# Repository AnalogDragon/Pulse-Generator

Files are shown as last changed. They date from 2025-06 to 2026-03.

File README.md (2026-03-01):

**Pulse Generator**  
  
[中文](./README-zh.md)  

Used for testing and calibrating dose rate instruments such as survey meters or calibrators. STM32G0, KiCad.  
  
This device was built because I purchased a LUDLUM Model 3 and a Model 2360, both of which require calibration of multiple threshold levels, so I made this small tool for that purpose.  
  
Functions:  
- 1. Generates adjustable pulses with amplitude 2 mV–1000 mV, pulse width 50 nS–500 µS, adjustable frequency, and selectable positive/negative polarity, for calibration or performance verification;  
- 2. Multiple operating modes;  
- 3. Output interface changed to MHV connector (previous low-quality BNC connectors could suffer dielectric breakdown);  
- 4. Supports USB power supply and battery power; when USB is connected, the battery is automatically disconnected;  

## Buttons  

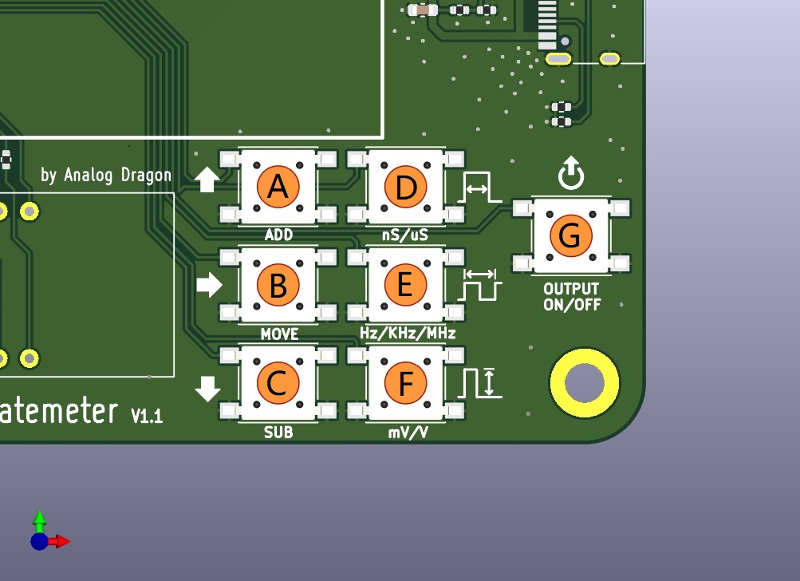
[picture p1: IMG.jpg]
keys
  

**Button function description**  

- A: **Increment** button. When a digit is selected, pressing it increases the value by +1;  
- B: **Select / Mode** button. **Short press** switches the selected digit position; **long press** switches the **mode** (see [Modes](#modes));  
- C: **Decrement** button. When a digit is selected, pressing it decreases the value by −1;  
- D: **Pulse Width** button. Short press to set, long press to change the multiplier. Range: 500 µS–50 nS, minimum step 50 nS, 4 significant digits;  
- E: **Frequency** button. Short press to set, long press to change the multiplier. Range: 5 MHz–0.1 Hz, 3 or 4 significant digits;  
- F: **Voltage** button. Short press to set, long press to switch between **output pulse voltage** and **input high-voltage value**;  
- G: **Output** button. Press to start outputting the configured pulses;  

***Other operations***  
- A + B: Switch output pulse polarity to **positive polarity** pulses (display shows `POS_┌┐_`)  
- C + B: Switch output pulse polarity to **negative polarity** pulses (display shows `NEG‾└┘‾`)  

***High-voltage calibration***  
How to enter: during power-on, hold F + B to enter calibration mode.  

Single-point calibration by default. You can press D / E / F to switch the number of calibration points to 1 / 3 / 5 (updated in V1.2).  
During calibration, adjust the displayed voltage to match the input voltage. Keep the voltage unchanged, then long-press the **Output** button (G) to save the calibration point.  
After the required number of calibration points is saved, calibration ends automatically. If the result displays `DONE`, calibration is successful. If `FAILED RETRY` is displayed, calibration has failed.  

Possible reasons for calibration failure:  
- The voltage difference between calibration points is less than 100 V (for example, point 1 is 100 V and point 2 is 150 V);  
- No input voltage during calibration;  
- The input voltage is not correlated with the displayed voltage;  

## Modes  

Three modes are supported:  

- Normal mode (`NORMAL MODE`): the configured parameters output **continuous** pulses. During output, a rapidly blinking indicator appears at the lower-right corner of the display to show status;  
- Repeat burst mode (`REPEAT BURST`): the configured parameters are output at **100 CPS**;  
- Single burst mode (`SINGEL BURST`): with the configured parameters, each press of the **Output** button generates exactly **100 pulses**;  

## Schematic  

[Schematic](./SCH.pdf)  

## Hardware  

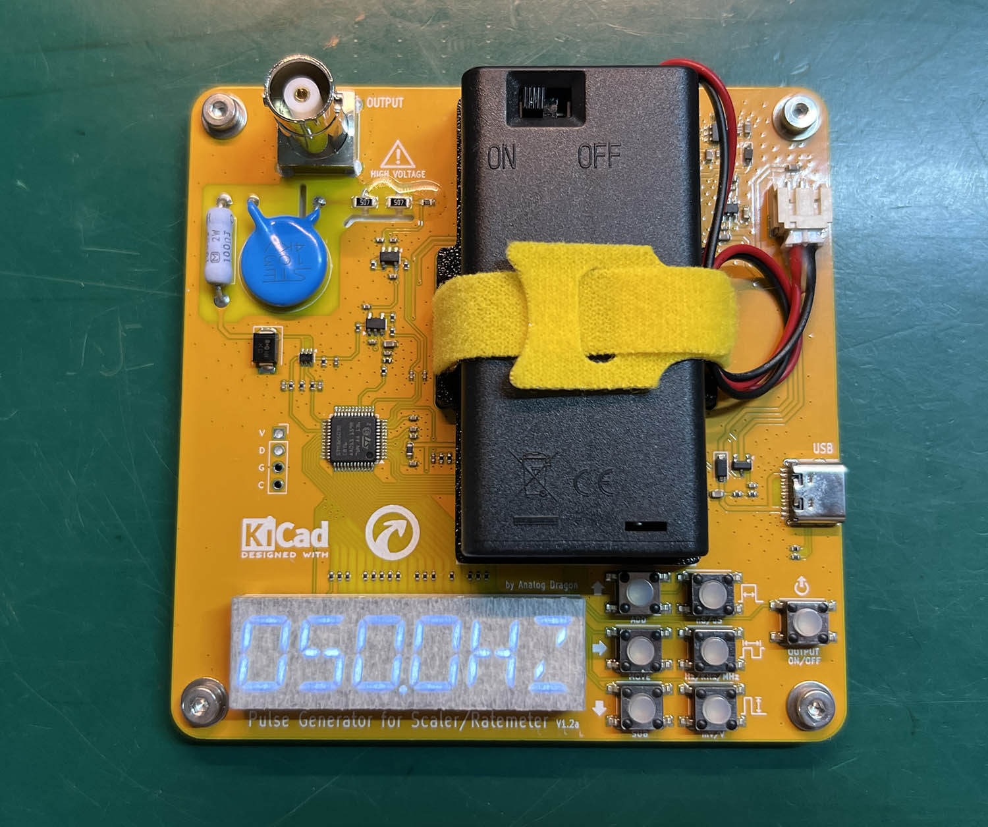
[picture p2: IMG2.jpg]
  

## TEST  
- Normal mode set 1.67CPS(100KCPM)  
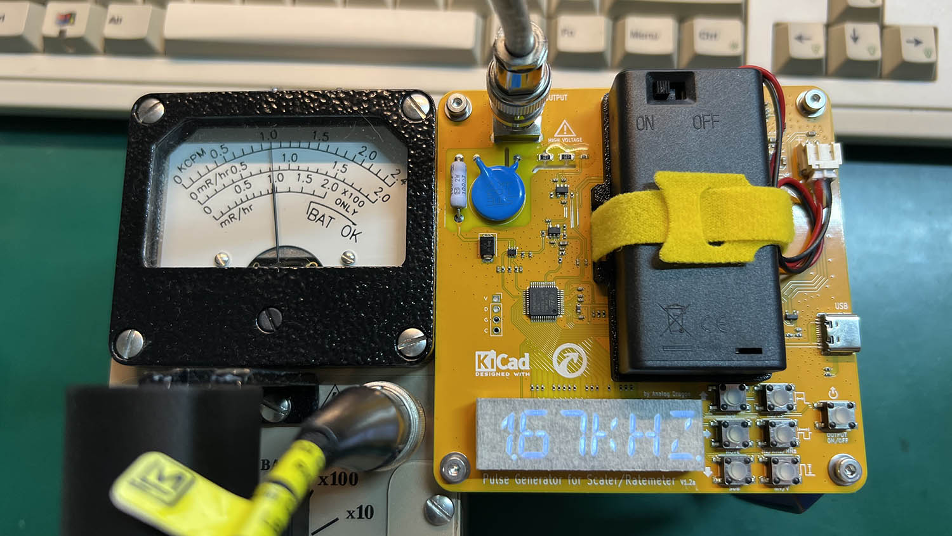
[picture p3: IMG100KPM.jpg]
  
  
- Repeat burst mode (6KCPM)  
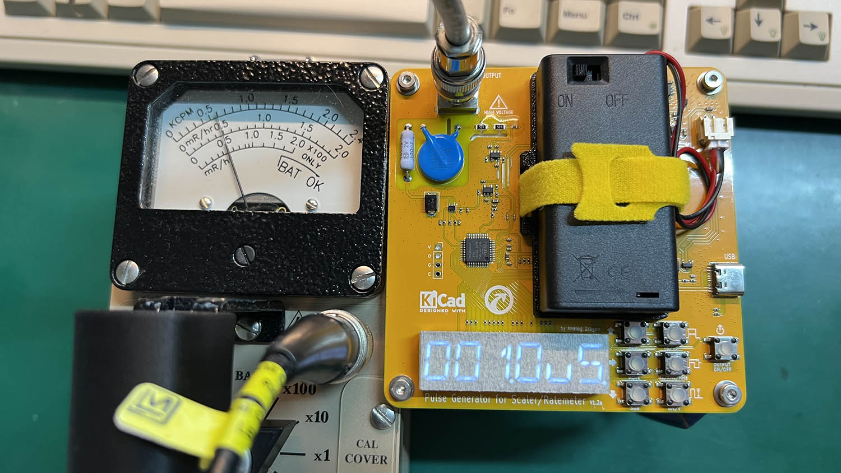
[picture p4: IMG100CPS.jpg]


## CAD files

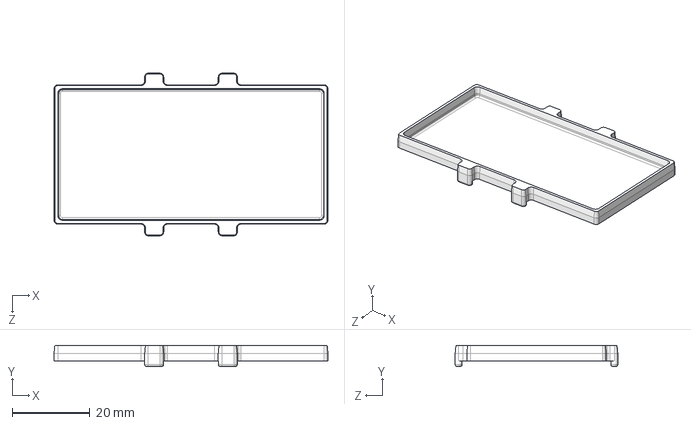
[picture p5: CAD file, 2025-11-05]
3D/电池盒限位small.STEP
70.4 x 5.40 x 41.8 mm

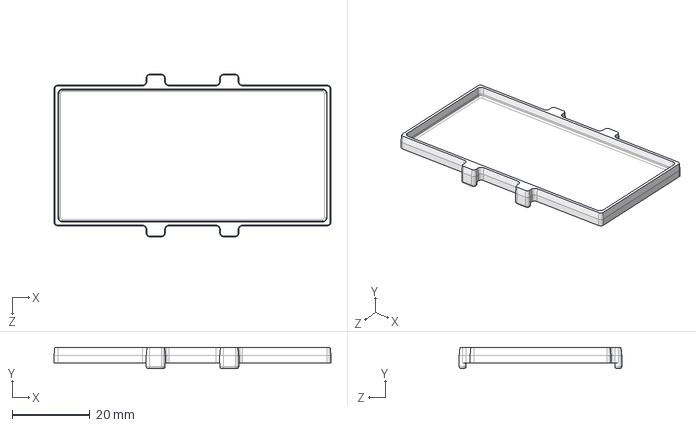
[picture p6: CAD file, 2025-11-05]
3D/电池盒限位.STEP
71.2 x 5.40 x 41.8 mm

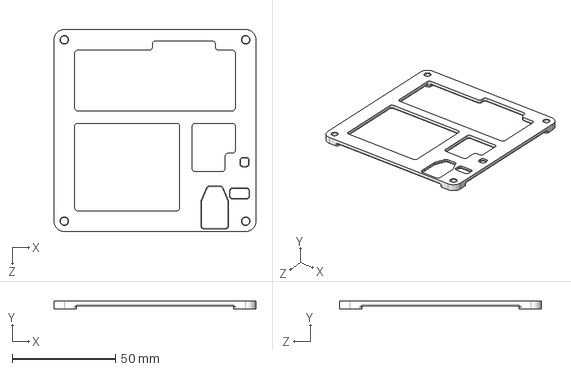
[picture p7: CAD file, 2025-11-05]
3D/底部支架.STEP
98.0 x 4.00 x 98.0 mm

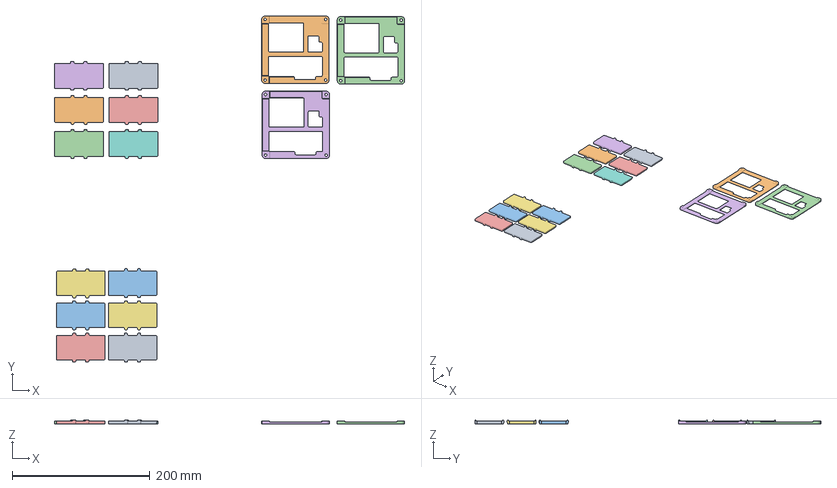
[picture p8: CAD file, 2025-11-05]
3D/print3D.3mf
508.8 x 502.4 x 5.40 mm
零件1.3.STEP x 6
底部支架.STEP x 3
电池盒限位small.STEP x 6

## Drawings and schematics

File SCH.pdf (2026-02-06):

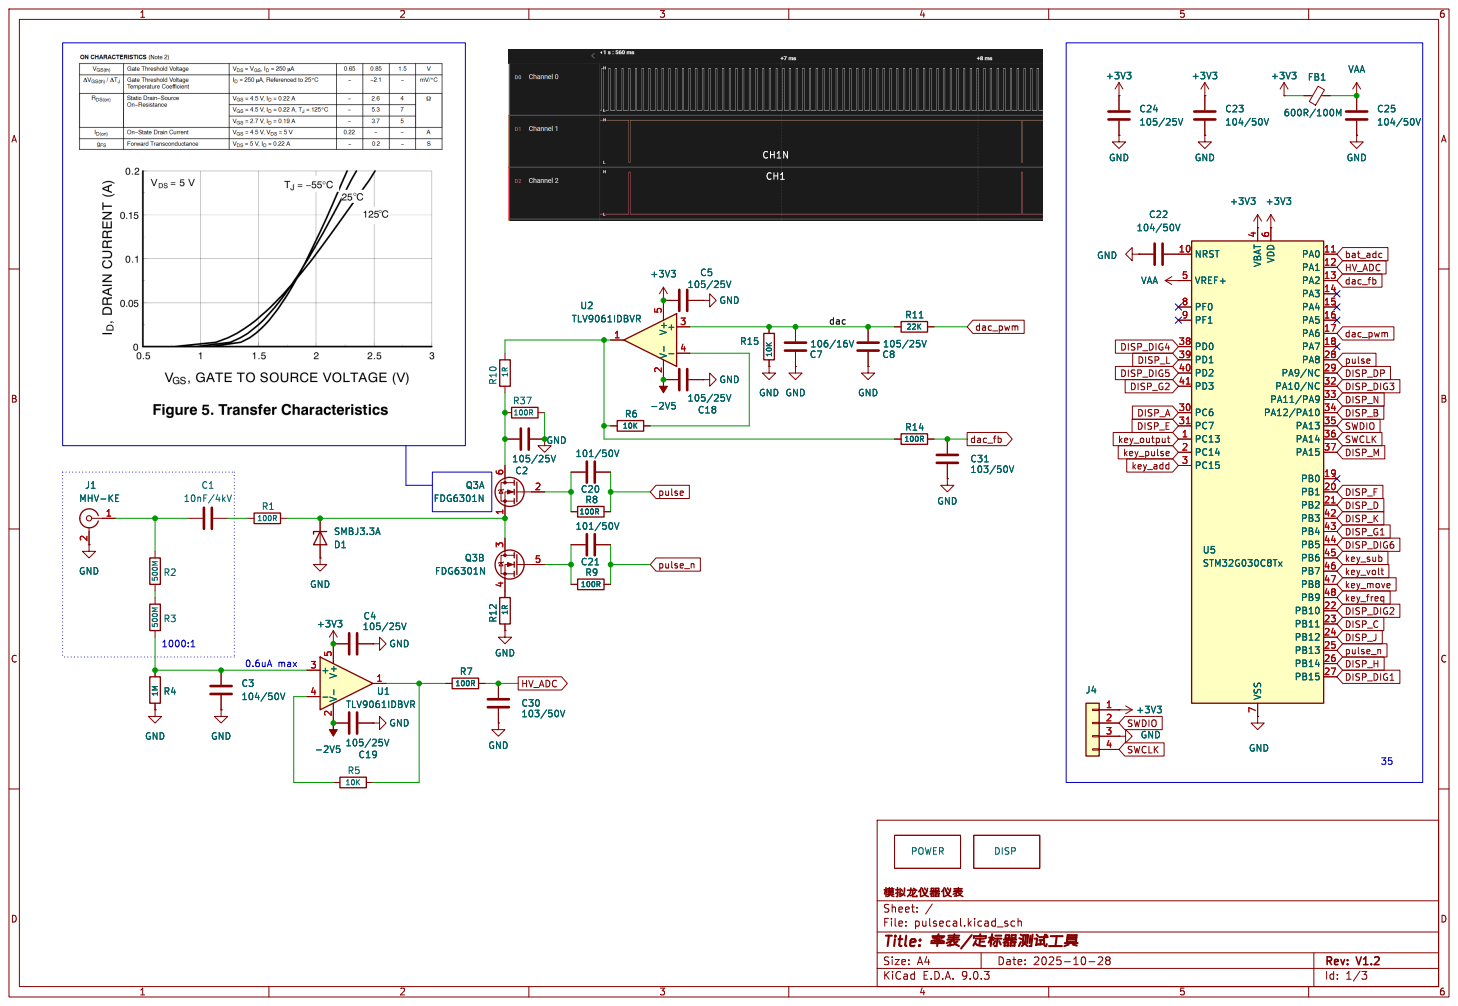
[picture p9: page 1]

File: pulsecal.kicad_sch Sheet: / þÿj!bßŸ™NêVhNêˆh

Id: 1/3 Title: þÿs‡ˆh/[šhVhmK‹Õ]åQw

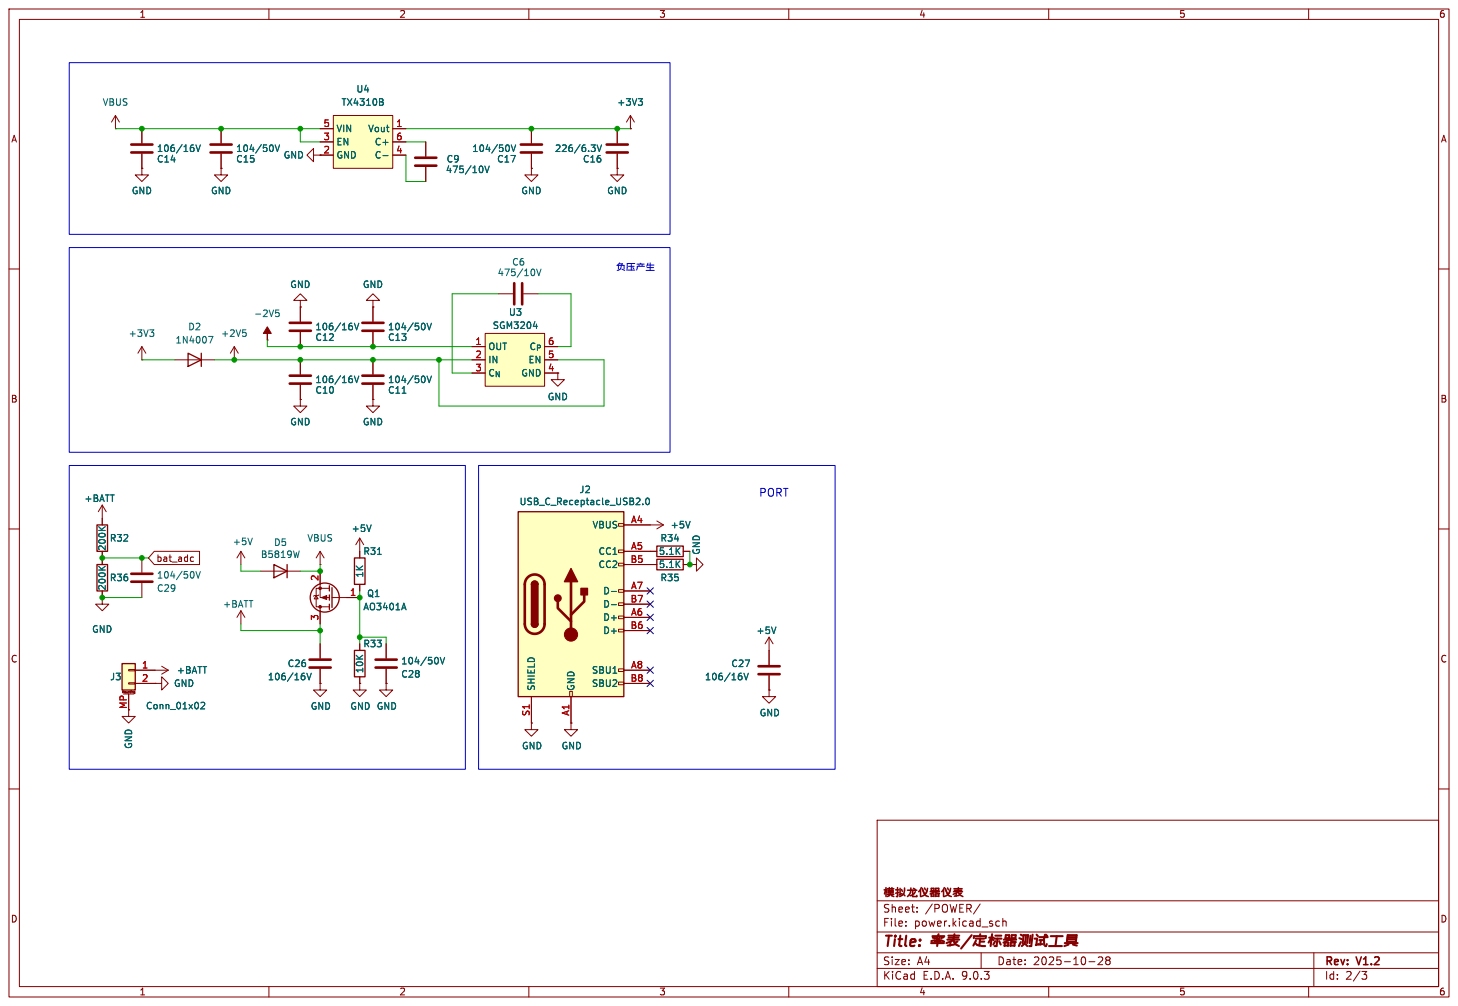
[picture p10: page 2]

File: power.kicad_sch Sheet: /POWER/ þÿj!bßŸ™NêVhNêˆh GND

Id: 2/3 Title: þÿs‡ˆh/[šhVhmK‹Õ]åQw

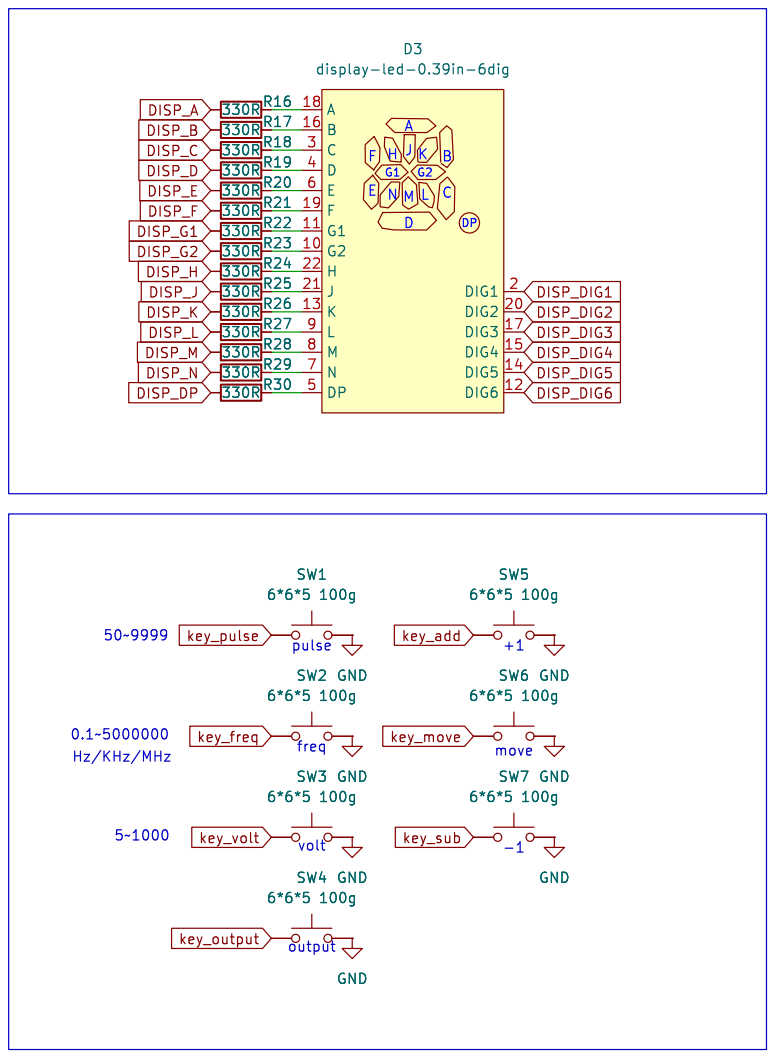
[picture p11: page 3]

6*6*5 100g GND GND GND GND

File: disp.kicad_sch Sheet: /DISP/ þÿj!bßŸ™NêVhNêˆh

Id: 3/3 Title: þÿs‡ˆh/[šhVhmK‹Õ]åQw

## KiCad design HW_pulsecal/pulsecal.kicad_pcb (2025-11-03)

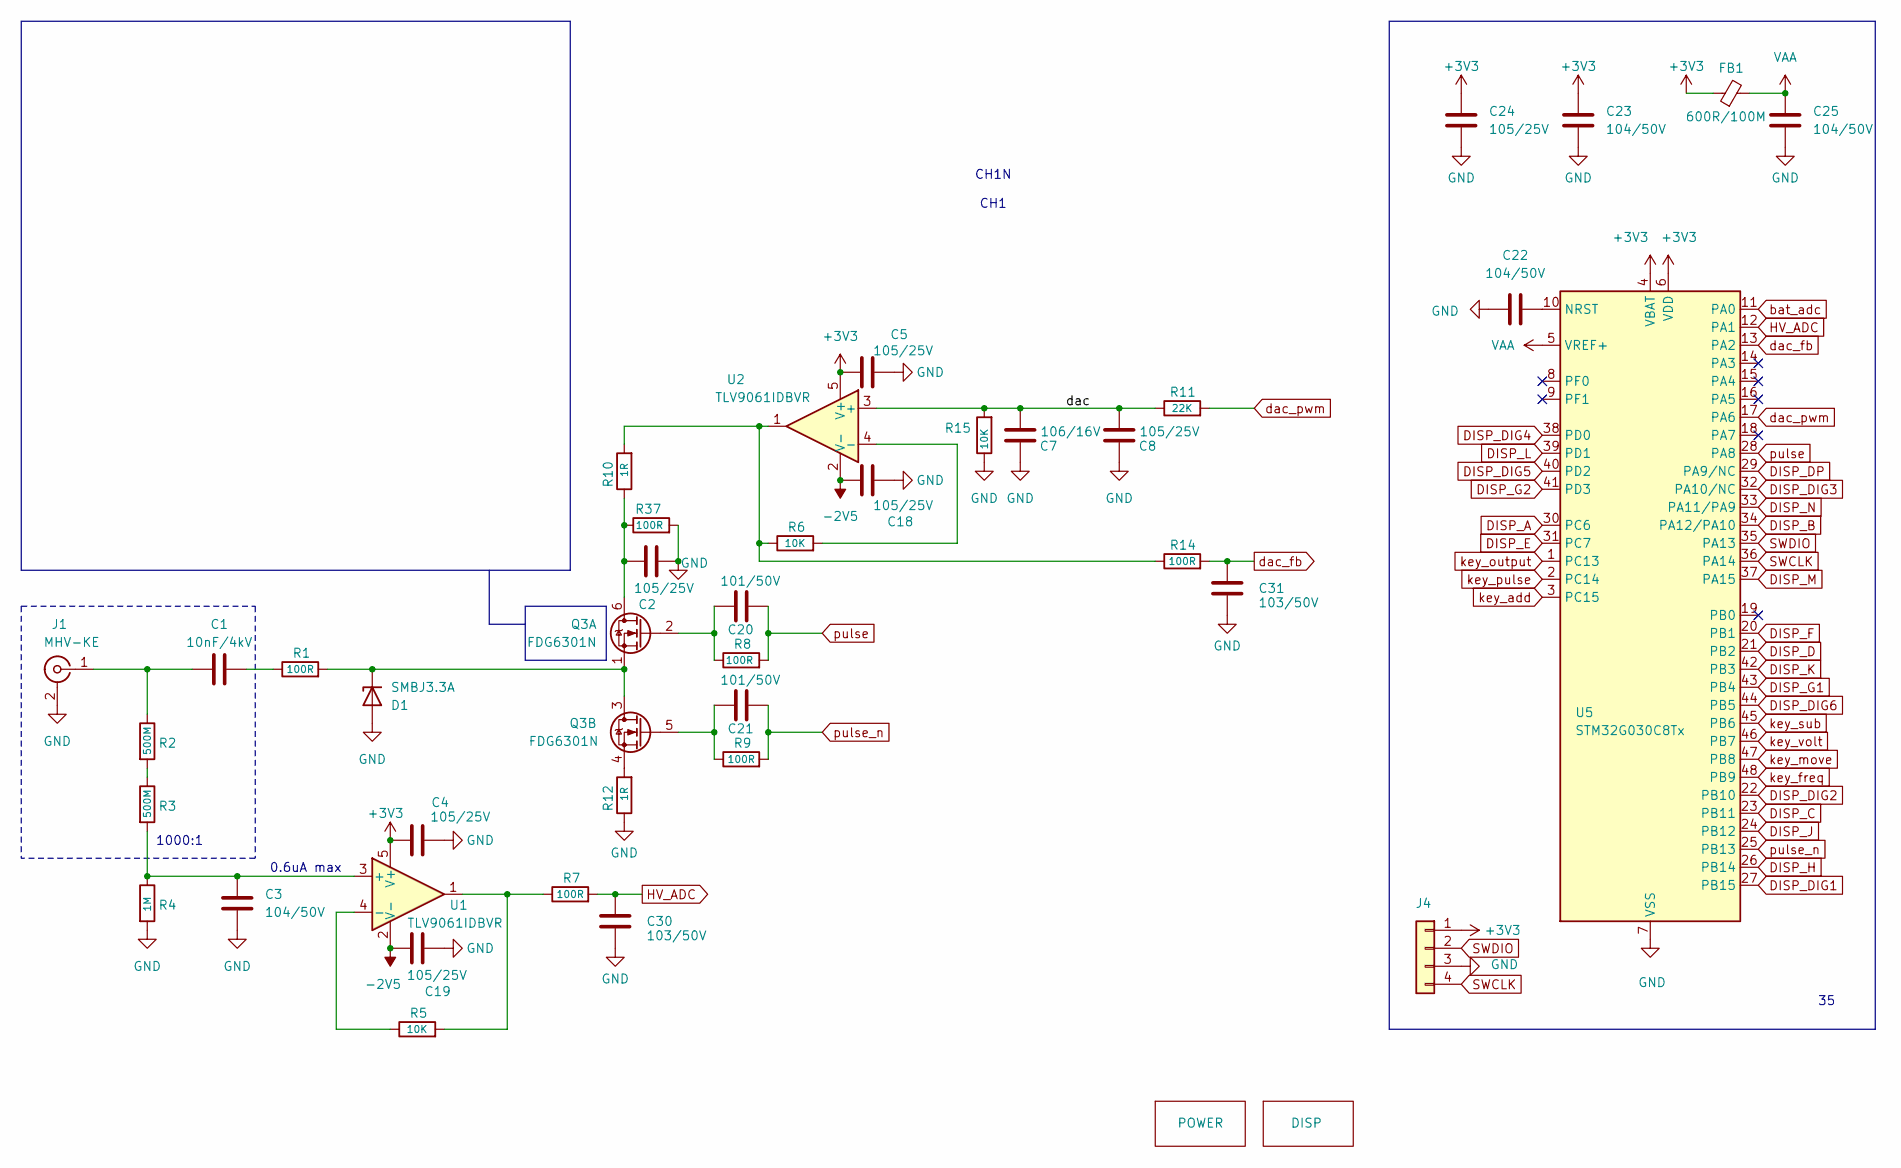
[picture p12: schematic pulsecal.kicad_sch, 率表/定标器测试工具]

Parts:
C1: 10nF/4kV; C_Rect_L13.5mm_W4.0mm_P10.00mm_FKS3_FKP3_MKS4
C2, C4, C5, C8, C18, C19, C24: 105/25V; C_0402_1005Metric
C3, C22, C23, C25: 104/50V; C_0402_1005Metric
C7: 106/16V; C_0603_1608Metric
C20, C21: 101/50V; C_0402_1005Metric
C30, C31: 103/50V; C_0402_1005Metric
D1: SMBJ3.3A; D_SMB
FB1: 600R/100M; L_0603_1608Metric
J1: MHV-KE; BNC_TEConnectivity_1478204_Vertical
J4: Conn_01x04; PinSocket_1x04_P2.54mm_Vertical
Q3: FDG6301N; SOT-363_SC-70-6
R1: 100R; R_Axial_DIN0411_L9.9mm_D3.6mm_P15.24mm_Horizontal
R2, R3: 500M; R_1206_3216Metric
R4: 1M; R_0603_1608Metric
R5, R6, R15: 10K; R_0402_1005Metric
R7, R8, R9, R14, R37: 100R; R_0402_1005Metric
R10, R12: 1R; R_0402_1005Metric
R11: 22K; R_0402_1005Metric
U1, U2: TLV9061IDBVR; SOT-23-5
U5: STM32G030C8Tx; LQFP-48_7x7mm_P0.5mm

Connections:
+3V3: C4.1, C5.1, C23.2, C24.2, FB1.1, J4.1, U1.5 (V+), U2.5 (V+), U5.4 (VBAT), U5.6 (VDD); also elsewhere on the board
-2V5: C18.1, C19.1, U1.2 (V-), U2.2 (V-); also elsewhere on the board
/dac: C7.2, C8.2, R11.1, R15.2, U2.3 (+)
DISP_A: U5.30 (PC6); also elsewhere on the board
DISP_B: U5.34 (PA12/PA10); also elsewhere on the board
DISP_C: U5.23 (PB11); also elsewhere on the board
DISP_D: U5.21 (PB2); also elsewhere on the board
DISP_DIG1: U5.27 (PB15); also elsewhere on the board
DISP_DIG2: U5.22 (PB10); also elsewhere on the board
DISP_DIG3: U5.32 (PA10/NC); also elsewhere on the board
DISP_DIG4: U5.38 (PD0); also elsewhere on the board
DISP_DIG5: U5.40 (PD2); also elsewhere on the board
DISP_DIG6: U5.44 (PB5); also elsewhere on the board
DISP_DP: U5.29 (PA9/NC); also elsewhere on the board
DISP_E: U5.31 (PC7); also elsewhere on the board
DISP_F: U5.20 (PB1); also elsewhere on the board
DISP_G1: U5.43 (PB4); also elsewhere on the board
DISP_G2: U5.41 (PD3); also elsewhere on the board
DISP_H: U5.26 (PB14); also elsewhere on the board
DISP_J: U5.24 (PB12); also elsewhere on the board
DISP_K: U5.42 (PB3); also elsewhere on the board
DISP_L: U5.39 (PD1); also elsewhere on the board
DISP_M: U5.37 (PA15); also elsewhere on the board
DISP_N: U5.33 (PA11/PA9); also elsewhere on the board
GND: C2.2, C3.2, C4.2, C5.2, C7.1, C8.1, C18.2, C19.2, C22.1, C23.1, C24.1, C25.1, C30.1, C31.1, D1.2 (A), J1.2 (Ext), J4.3, R4.2, R12.1, R15.1, R37.2, U5.7 (VSS); also elsewhere on the board
HV_ADC: C30.2, R7.2, U5.12 (PA1)
unnamed: C1.2, R1.1
unnamed: D1.1 (K), Q3.1 (S), Q3.3 (D), R1.2
unnamed: C1.1, J1.1 (In), R2.1
unnamed: C2.1, Q3.6 (D), R10.1, R37.1
unnamed: C20.2, Q3.2 (G), R8.1
unnamed: C21.2, Q3.5 (G), R9.1
unnamed: Q3.4 (S), R12.2
unnamed: R2.2, R3.1
unnamed: R5.2, R7.1, U1.1
unnamed: R6.1, R10.2, R14.1, U2.1
unnamed: C3.1, R3.2, R4.1, U1.3 (+)
unnamed: R5.1, U1.4 (-)
unnamed: R6.2, U2.4 (-)
unnamed: C22.2, U5.10 (NRST)
SWCLK: J4.4, U5.36 (PA14)
SWDIO: J4.2, U5.35 (PA13)
VAA: C25.2, FB1.2, U5.5 (VREF+)
bat_adc: U5.11 (PA0); also elsewhere on the board
dac_fb: C31.2, R14.2, U5.13 (PA2)
dac_pwm: R11.2, U5.17 (PA6)
key_add: U5.3 (PC15); also elsewhere on the board
key_freq: U5.48 (PB9); also elsewhere on the board
key_move: U5.47 (PB8); also elsewhere on the board
key_output: U5.1 (PC13); also elsewhere on the board
key_pulse: U5.2 (PC14); also elsewhere on the board
key_sub: U5.45 (PB6); also elsewhere on the board
key_volt: U5.46 (PB7); also elsewhere on the board
pulse: C20.1, R8.2, U5.28 (PA8)
pulse_n: C21.1, R9.2, U5.25 (PB13)

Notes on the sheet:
0.6uA max
CH1N CH1
1000:1

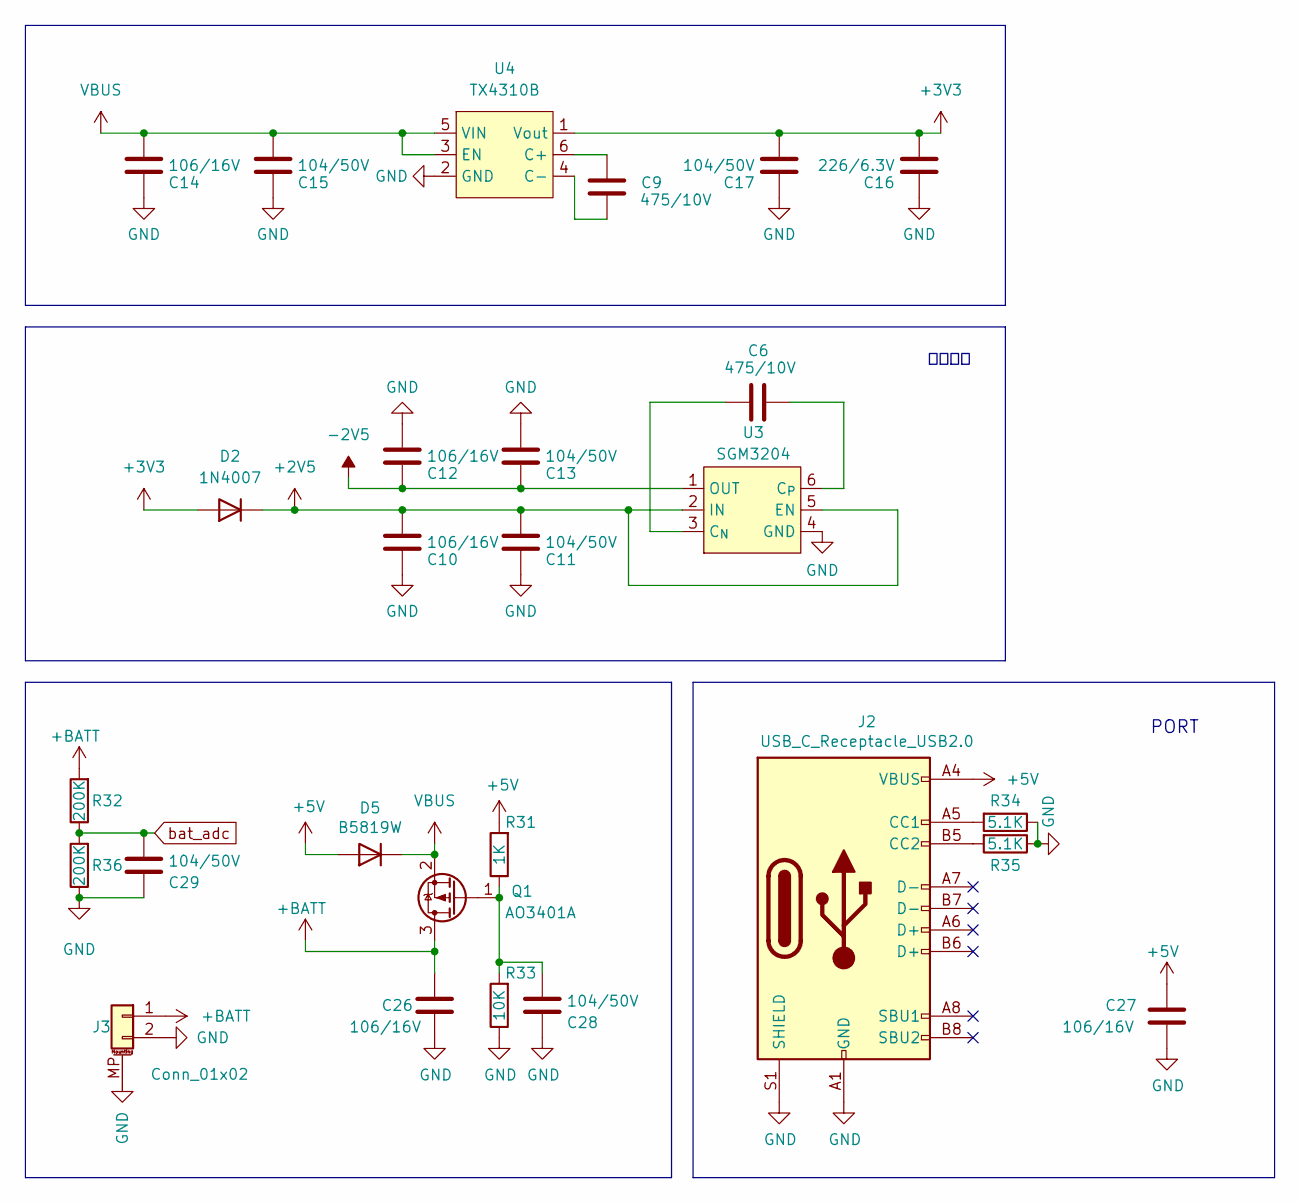
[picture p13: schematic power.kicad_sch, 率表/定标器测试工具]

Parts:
C6, C9: 475/10V; C_0603_1608Metric
C10, C12, C14, C26, C27: 106/16V; C_0603_1608Metric
C11, C13, C15, C17, C28, C29: 104/50V; C_0402_1005Metric
C16: 226/6.3V; C_0603_1608Metric
D2: 1N4007; D_SOD-323_HandSoldering
D5: B5819W; D_SOD-123
J2: USB_C_Receptacle_USB2.0; USB_C_Receptacle_HRO_TYPE-C-31-M-12
J3: Conn_01x02; JST_PH_S2B-PH-SM4-TB_1x02-1MP_P2.00mm_Horizontal
Q1: AO3401A; SOT-23
R31: 1K; R_0402_1005Metric
R32, R36: 200K; R_0402_1005Metric
R33: 10K; R_0402_1005Metric
R34, R35: 5.1K; R_0402_1005Metric
U3: SGM3204; SOT-23-6
U4: TX4310B; SOT-23-6

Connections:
+2V5: C10.1, C11.1, D2.1 (K), U3.2 (IN), U3.5 (EN)
+3V3: C16.1, C17.1, D2.2 (A), U4.1 (Vout); also elsewhere on the board
+5V: C27.1, D5.2 (A), J2.A4 (VBUS), J2.A9 (VBUS), J2.B4 (VBUS), J2.B9 (VBUS), R31.2
+BATT: C26.1, J3.1, Q1.3 (D), R32.2
-2V5: C12.2, C13.2, U3.1 (OUT); also elsewhere on the board
GND: C10.2, C11.2, C12.1, C13.1, C14.2, C15.2, C16.2, C17.2, C26.2, C27.2, C28.2, C29.2, J2.A1 (GND), J2.A12 (GND), J2.B1 (GND), J2.B12 (GND), J2.S1 (SHIELD), J3.2, J3.MP (MountPin), R33.1, R34.1, R35.1, R36.1, U3.4 (GND), U4.2 (GND); also elsewhere on the board
unnamed: J2.A5 (CC1), R34.2
unnamed: J2.B5 (CC2), R35.2
unnamed: C28.1, Q1.1 (G), R31.1, R33.2
unnamed: C6.2, U3.3 (C_{N})
unnamed: C6.1, U3.6 (C_{P})
unnamed: C9.1, U4.6 (C+)
unnamed: C9.2, U4.4 (C-)
VBUS: C14.1, C15.1, D5.1 (K), Q1.2 (S), U4.3 (EN), U4.5 (VIN)
bat_adc: C29.1, R32.1, R36.2; also elsewhere on the board

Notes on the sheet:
PORT
负压产生

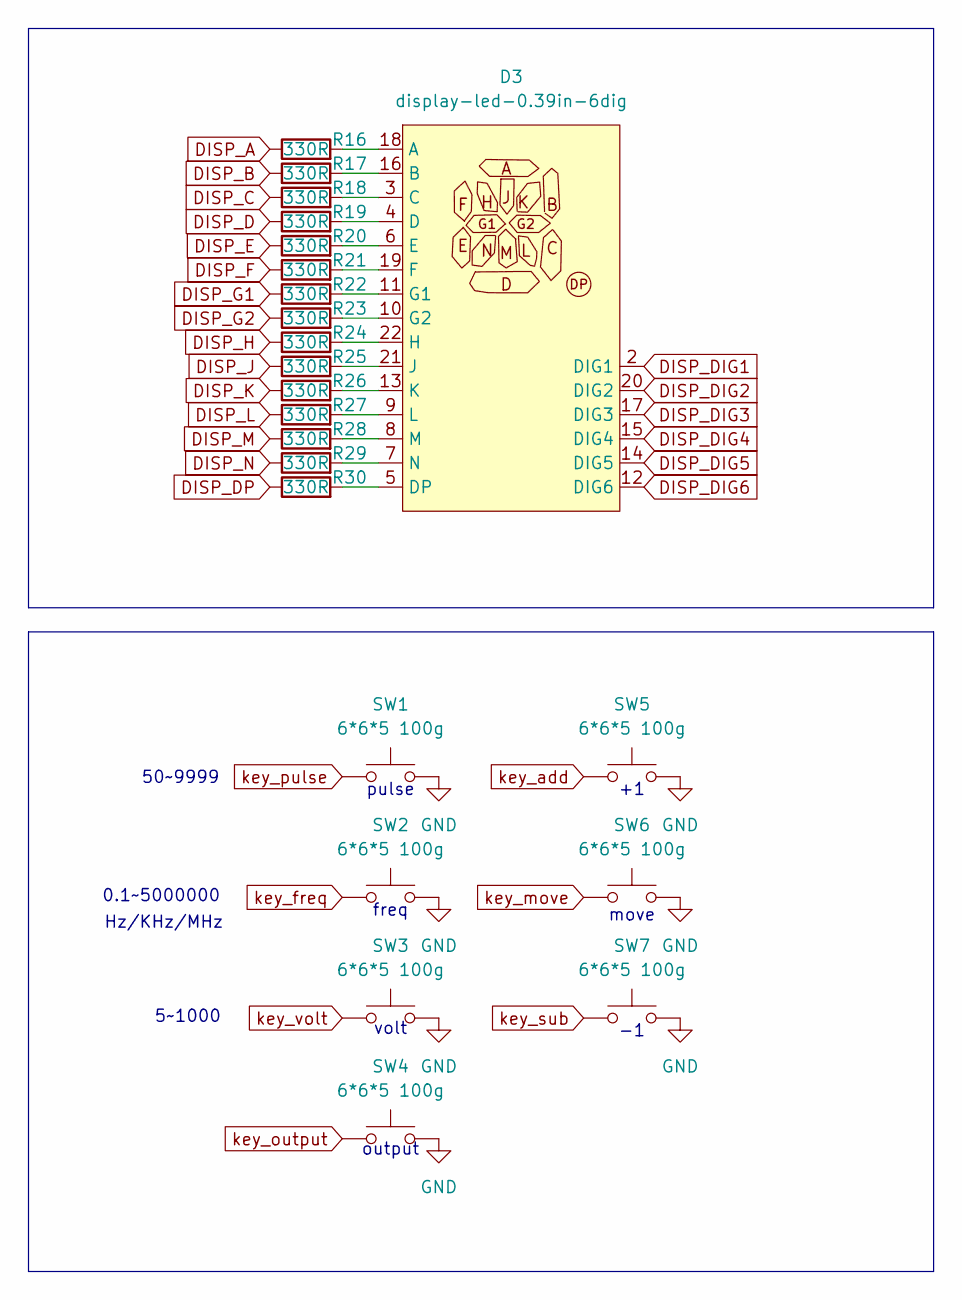
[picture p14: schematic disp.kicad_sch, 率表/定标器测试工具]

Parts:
D3: display-led-0.39in-6dig
R16, R17, R18, R19, R20, R21, R22, R23, R24, R25, R26, R27, R28, R29, R30: 330R; R_0402_1005Metric
SW1, SW2, SW3, SW4, SW5, SW6, SW7: 6*6*5 100g; SW_SPST_PTS645

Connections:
DISP_A: R16.1; also elsewhere on the board
DISP_B: R17.1; also elsewhere on the board
DISP_C: R18.1; also elsewhere on the board
DISP_D: R19.1; also elsewhere on the board
DISP_DIG1: D3.2 (DIG1); also elsewhere on the board
DISP_DIG2: D3.20 (DIG2); also elsewhere on the board
DISP_DIG3: D3.17 (DIG3); also elsewhere on the board
DISP_DIG4: D3.15 (DIG4); also elsewhere on the board
DISP_DIG5: D3.14 (DIG5); also elsewhere on the board
DISP_DIG6: D3.12 (DIG6); also elsewhere on the board
DISP_DP: R30.1; also elsewhere on the board
DISP_E: R20.1; also elsewhere on the board
DISP_F: R21.1; also elsewhere on the board
DISP_G1: R22.1; also elsewhere on the board
DISP_G2: R23.1; also elsewhere on the board
DISP_H: R24.1; also elsewhere on the board
DISP_J: R25.1; also elsewhere on the board
DISP_K: R26.1; also elsewhere on the board
DISP_L: R27.1; also elsewhere on the board
DISP_M: R28.1; also elsewhere on the board
DISP_N: R29.1; also elsewhere on the board
GND: SW1.2, SW2.2, SW3.2, SW4.2, SW5.2, SW6.2, SW7.2; also elsewhere on the board
unnamed: D3.18 (A), R16.2
unnamed: D3.16 (B), R17.2
unnamed: D3.3 (C), R18.2
unnamed: D3.4 (D), R19.2
unnamed: D3.5 (DP), R30.2
unnamed: D3.6 (E), R20.2
unnamed: D3.19 (F), R21.2
unnamed: D3.11 (G1), R22.2
unnamed: D3.10 (G2), R23.2
unnamed: D3.22 (H), R24.2
unnamed: D3.21 (J), R25.2
unnamed: D3.13 (K), R26.2
unnamed: D3.9 (L), R27.2
unnamed: D3.8 (M), R28.2
unnamed: D3.7 (N), R29.2
key_add: SW5.1; also elsewhere on the board
key_freq: SW2.1; also elsewhere on the board
key_move: SW6.1; also elsewhere on the board
key_output: SW4.1; also elsewhere on the board
key_pulse: SW1.1; also elsewhere on the board
key_sub: SW7.1; also elsewhere on the board
key_volt: SW3.1; also elsewhere on the board

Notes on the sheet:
output
freq
50~9999
volt
0.1~5000000
5~1000
Hz/KHz/MHz
pulse
move

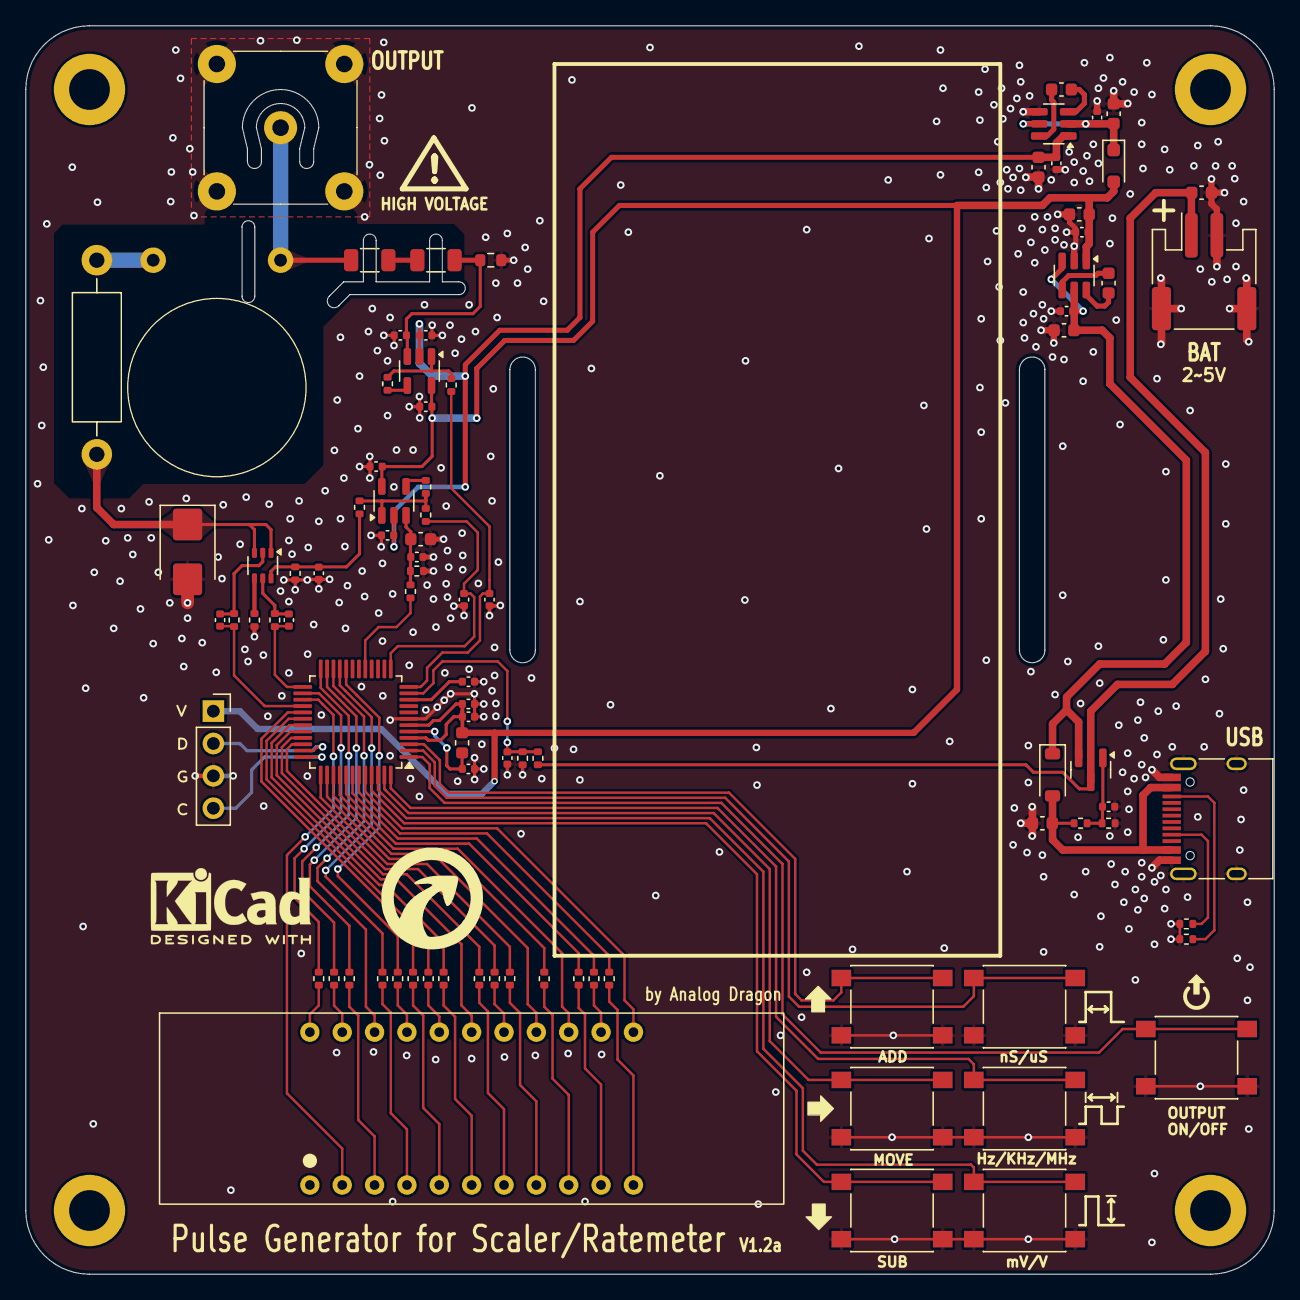
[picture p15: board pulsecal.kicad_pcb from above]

Board: 2 copper layers, 98.0 x 98.0 mm, 90 parts (0 on the bottom side), 81 nets.

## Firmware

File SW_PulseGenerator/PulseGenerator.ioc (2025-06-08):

#MicroXplorer Configuration settings - do not modify
ADC1.Channel-40\#ChannelRegularConversion=ADC_CHANNEL_0
ADC1.Channel-41\#ChannelRegularConversion=ADC_CHANNEL_1
ADC1.Channel-42\#ChannelRegularConversion=ADC_CHANNEL_2
ADC1.Channel-43\#ChannelRegularConversion=ADC_CHANNEL_VREFINT
ADC1.ClockPrescaler=ADC_CLOCK_SYNC_PCLK_DIV4
ADC1.ContinuousConvMode=ENABLE
ADC1.DMAContinuousRequests=ENABLE
ADC1.DataAlign=ADC_DATAALIGN_RIGHT
ADC1.DiscontinuousConvMode=DISABLE
ADC1.EOCSelection=ADC_EOC_SINGLE_CONV
ADC1.IPParameters=NbrOfConversionFlag,master,SelectedChannel,SamplingTimeCommon1,NbrOfConversion,DMAContinuousRequests,Sequencer,ContinuousConvMode,EOCSelection,Overrun,DataAlign,ClockPrescaler,DiscontinuousConvMode,Rank-40\#ChannelRegularConversion,Channel-40\#ChannelRegularConversion,SamplingTime-40\#ChannelRegularConversion,Rank-41\#ChannelRegularConversion,Channel-41\#ChannelRegularConversion,SamplingTime-41\#ChannelRegularConversion,Rank-42\#ChannelRegularConversion,Channel-42\#ChannelRegularConversion,SamplingTime-42\#ChannelRegularConversion,Rank-43\#ChannelRegularConversion,Channel-43\#ChannelRegularConversion,SamplingTime-43\#ChannelRegularConversion,SamplingTimeCommon2
ADC1.NbrOfConversion=4
ADC1.NbrOfConversionFlag=1
ADC1.Overrun=ADC_OVR_DATA_PRESERVED
ADC1.Rank-40\#ChannelRegularConversion=1
ADC1.Rank-41\#ChannelRegularConversion=2
ADC1.Rank-42\#ChannelRegularConversion=3
ADC1.Rank-43\#ChannelRegularConversion=4
ADC1.SamplingTime-40\#ChannelRegularConversion=ADC_SAMPLINGTIME_COMMON_1
ADC1.SamplingTime-41\#ChannelRegularConversion=ADC_SAMPLINGTIME_COMMON_1
ADC1.SamplingTime-42\#ChannelRegularConversion=ADC_SAMPLINGTIME_COMMON_1
ADC1.SamplingTime-43\#ChannelRegularConversion=ADC_SAMPLINGTIME_COMMON_1
ADC1.SamplingTimeCommon1=ADC_SAMPLETIME_160CYCLES_5
ADC1.SamplingTimeCommon2=ADC_SAMPLETIME_160CYCLES_5
ADC1.SelectedChannel=ADC_CHANNEL_0|ADC_CHANNEL_1|ADC_CHANNEL_2|ADC_CHANNEL_VREFINT
ADC1.Sequencer=FULLY_CONFIGURABLE
ADC1.master=1
CAD.formats=
CAD.pinconfig=
CAD.provider=
Dma.ADC1.0.Direction=DMA_PERIPH_TO_MEMORY
Dma.ADC1.0.EventEnable=DISABLE
Dma.ADC1.0.Instance=DMA1_Channel1
Dma.ADC1.0.MemDataAlignment=DMA_MDATAALIGN_HALFWORD
Dma.ADC1.0.MemInc=DMA_MINC_ENABLE
Dma.ADC1.0.Mode=DMA_CIRCULAR
Dma.ADC1.0.PeriphDataAlignment=DMA_PDATAALIGN_HALFWORD
Dma.ADC1.0.PeriphInc=DMA_PINC_DISABLE
Dma.ADC1.0.Polarity=HAL_DMAMUX_REQ_GEN_RISING
Dma.ADC1.0.Priority=DMA_PRIORITY_LOW
Dma.ADC1.0.RequestNumber=1
Dma.ADC1.0.RequestParameters=Instance,Direction,PeriphInc,MemInc,PeriphDataAlignment,MemDataAlignment,Mode,Priority,SignalID,Polarity,RequestNumber,SyncSignalID,SyncPolarity,SyncEnable,EventEnable,SyncRequestNumber
Dma.ADC1.0.SignalID=NONE
Dma.ADC1.0.SyncEnable=DISABLE
Dma.ADC1.0.SyncPolarity=HAL_DMAMUX_SYNC_NO_EVENT
Dma.ADC1.0.SyncRequestNumber=1
Dma.ADC1.0.SyncSignalID=NONE
Dma.Request0=ADC1
Dma.RequestsNb=1
File.Version=6
GPIO.groupedBy=Group By Peripherals
KeepUserPlacement=false
Mcu.CPN=STM32G030C6T6
Mcu.Family=STM32G0
Mcu.IP0=ADC1
Mcu.IP1=DMA
Mcu.IP2=NVIC
Mcu.IP3=RCC
Mcu.IP4=SYS
Mcu.IP5=TIM1
Mcu.IP6=TIM3
Mcu.IP7=TIM14
Mcu.IP8=TIM16
Mcu.IP9=TIM17
Mcu.IPNb=10
Mcu.Name=STM32G030C(6-8)Tx
Mcu.Package=LQFP48
Mcu.Pin0=PC13
Mcu.Pin1=PC14-OSC32_IN (PC14)
Mcu.Pin10=PB11
Mcu.Pin11=PB12
Mcu.Pin12=PB13
Mcu.Pin13=PB14
Mcu.Pin14=PB15
Mcu.Pin15=PA8
Mcu.Pin16=PA9
Mcu.Pin17=PC6
Mcu.Pin18=PC7
Mcu.Pin19=PA10
Mcu.Pin2=PC15-OSC32_OUT (PC15)
Mcu.Pin20=PA11 [PA9]
Mcu.Pin21=PA12 [PA10]
Mcu.Pin22=PA13
Mcu.Pin23=PA14-BOOT0
Mcu.Pin24=PA15
Mcu.Pin25=PD0
Mcu.Pin26=PD1
Mcu.Pin27=PD2
Mcu.Pin28=PD3
Mcu.Pin29=PB3
Mcu.Pin3=PA0
Mcu.Pin30=PB4
Mcu.Pin31=PB5
Mcu.Pin32=PB6
Mcu.Pin33=PB7
Mcu.Pin34=PB8
Mcu.Pin35=PB9
Mcu.Pin36=VP_ADC1_Vref_Input
Mcu.Pin37=VP_SYS_VS_Systick
Mcu.Pin38=VP_TIM1_VS_ClockSourceINT
Mcu.Pin39=VP_TIM1_VS_OPM
Mcu.Pin4=PA1
Mcu.Pin40=VP_TIM3_VS_ControllerModeTrigger
Mcu.Pin41=VP_TIM3_VS_ClockSourceINT
Mcu.Pin42=VP_TIM3_VS_ClockSourceITR
Mcu.Pin43=VP_TIM14_VS_ClockSourceINT
Mcu.Pin44=VP_TIM16_VS_ClockSourceINT
Mcu.Pin45=VP_TIM17_VS_ClockSourceINT
Mcu.Pin5=PA2
Mcu.Pin6=PA6
Mcu.Pin7=PB1
Mcu.Pin8=PB2
Mcu.Pin9=PB10
Mcu.PinsNb=46
Mcu.ThirdPartyNb=0
Mcu.UserConstants=
Mcu.UserName=STM32G030C6Tx
MxCube.Version=6.14.1
MxDb.Version=DB.6.0.141
NVIC.DMA1_Channel1_IRQn=true\:3\:0\:true\:false\:true\:false\:true\:true
NVIC.ForceEnableDMAVector=true
NVIC.HardFault_IRQn=true\:0\:0\:false\:false\:true\:false\:false\:false
NVIC.NonMaskableInt_IRQn=true\:0\:0\:false\:false\:true\:false\:false\:false
NVIC.PendSV_IRQn=true\:0\:0\:false\:false\:true\:false\:false\:false
NVIC.SVC_IRQn=true\:0\:0\:false\:false\:true\:false\:false\:true
NVIC.SysTick_IRQn=true\:3\:0\:false\:false\:true\:false\:true\:false
NVIC.TIM14_IRQn=true\:2\:0\:true\:false\:true\:true\:true\:true
NVIC.TIM17_IRQn=true\:0\:0\:true\:false\:true\:true\:true\:true
NVIC.TIM1_CC_IRQn=true\:0\:0\:false\:false\:true\:true\:true\:true
NVIC.TIM3_IRQn=true\:0\:0\:false\:false\:true\:true\:true\:true
PA0.Mode=IN0
PA0.Signal=ADC1_IN0
PA1.Mode=IN1
PA1.Signal=ADC1_IN1
PA10.GPIOParameters=GPIO_Label
PA10.GPIO_Label=DISP_DIG3
PA10.Locked=true
PA10.Signal=GPIO_Output
PA11\ [PA9].GPIOParameters=PinState,GPIO_Label
PA11\ [PA9].GPIO_Label=DISP_N
PA11\ [PA9].Locked=true
PA11\ [PA9].PinState=GPIO_PIN_SET
PA11\ [PA9].Signal=GPIO_Output
PA12\ [PA10].GPIOParameters=PinState,GPIO_Label
PA12\ [PA10].GPIO_Label=DISP_B
PA12\ [PA10].Locked=true
PA12\ [PA10].PinState=GPIO_PIN_SET
PA12\ [PA10].Signal=GPIO_Output
PA13.Mode=Serial_Wire
PA13.Signal=SYS_SWDIO
PA14-BOOT0.Mode=Serial_Wire
PA14-BOOT0.Signal=SYS_SWCLK
PA15.GPIOParameters=PinState,GPIO_Label
PA15.GPIO_Label=DISP_M
PA15.Locked=true
PA15.PinState=GPIO_PIN_SET
PA15.Signal=GPIO_Output
PA2.Mode=IN2
PA2.Signal=ADC1_IN2
PA6.GPIOParameters=GPIO_PuPd
PA6.GPIO_PuPd=GPIO_NOPULL
PA6.Locked=true
PA6.Signal=S_TIM16_CH1
PA8.GPIOParameters=GPIO_Speed,PinState,GPIO_PuPd
PA8.GPIO_PuPd=GPIO_PULLDOWN
PA8.GPIO_Speed=GPIO_SPEED_FREQ_MEDIUM
PA8.Locked=true
PA8.PinState=GPIO_PIN_RESET
PA8.Signal=S_TIM1_CH1
PA9.GPIOParameters=PinState,GPIO_Label
PA9.GPIO_Label=DISP_DP
PA9.Locked=true
PA9.PinState=GPIO_PIN_SET
PA9.Signal=GPIO_Output
PB1.GPIOParameters=PinState,GPIO_Label
PB1.GPIO_Label=DISP_F
PB1.Locked=true
PB1.PinState=GPIO_PIN_SET
PB1.Signal=GPIO_Output
PB10.GPIOParameters=GPIO_Label
PB10.GPIO_Label=DISP_DIG2
PB10.Locked=true
PB10.Signal=GPIO_Output
PB11.GPIOParameters=PinState,GPIO_Label
PB11.GPIO_Label=DISP_C
PB11.Locked=true
PB11.PinState=GPIO_PIN_SET
PB11.Signal=GPIO_Output
PB12.GPIOParameters=PinState,GPIO_Label
PB12.GPIO_Label=DISP_J
PB12.Locked=true
PB12.PinState=GPIO_PIN_SET
PB12.Signal=GPIO_Output
PB13.GPIOParameters=GPIO_Speed,PinState,GPIO_PuPd
PB13.GPIO_PuPd=GPIO_PULLUP
PB13.GPIO_Speed=GPIO_SPEED_FREQ_MEDIUM
PB13.Locked=true
PB13.Mode=PWM Generation1 CH1 CH1N
PB13.PinState=GPIO_PIN_SET
PB13.Signal=TIM1_CH1N
PB14.GPIOParameters=PinState,GPIO_Label
PB14.GPIO_Label=DISP_H
PB14.Locked=true
PB14.PinState=GPIO_PIN_SET
PB14.Signal=GPIO_Output
PB15.GPIOParameters=GPIO_Label
PB15.GPIO_Label=DISP_DIG1
PB15.Locked=true
PB15.Signal=GPIO_Output
PB2.GPIOParameters=PinState,GPIO_Label
PB2.GPIO_Label=DISP_D
PB2.Locked=true
PB2.PinState=GPIO_PIN_SET
PB2.Signal=GPIO_Output
PB3.GPIOParameters=PinState,GPIO_Label
PB3.GPIO_Label=DISP_K
PB3.Locked=true
PB3.PinState=GPIO_PIN_SET
PB3.Signal=GPIO_Output
PB4.GPIOParameters=PinState,GPIO_Label
PB4.GPIO_Label=DISP_G1
PB4.Locked=true
PB4.PinState=GPIO_PIN_SET
PB4.Signal=GPIO_Output
PB5.GPIOParameters=GPIO_Label
PB5.GPIO_Label=DISP_DIG6
PB5.Locked=true
PB5.Signal=GPIO_Output
PB6.GPIOParameters=GPIO_PuPd,GPIO_Label
PB6.GPIO_Label=key_sub
PB6.GPIO_PuPd=GPIO_PULLUP
PB6.Locked=true
PB6.Signal=GPIO_Input
PB7.GPIOParameters=GPIO_PuPd,GPIO_Label
PB7.GPIO_Label=key_volt
PB7.GPIO_PuPd=GPIO_PULLUP
PB7.Locked=true
PB7.Signal=GPIO_Input
PB8.GPIOParameters=GPIO_PuPd,GPIO_Label
PB8.GPIO_Label=key_move
PB8.GPIO_PuPd=GPIO_PULLUP
PB8.Locked=true
PB8.Signal=GPIO_Input
PB9.GPIOParameters=GPIO_PuPd,GPIO_Label
PB9.GPIO_Label=key_freq
PB9.GPIO_PuPd=GPIO_PULLUP
PB9.Locked=true
PB9.Signal=GPIO_Input
PC13.GPIOParameters=GPIO_PuPd,GPIO_Label
PC13.GPIO_Label=key_output
PC13.GPIO_PuPd=GPIO_PULLUP
PC13.Locked=true
PC13.Signal=GPIO_Input
PC14-OSC32_IN\ (PC14).GPIOParameters=GPIO_PuPd,GPIO_Label
PC14-OSC32_IN\ (PC14).GPIO_Label=key_pulse
PC14-OSC32_IN\ (PC14).GPIO_PuPd=GPIO_PULLUP
PC14-OSC32_IN\ (PC14).Locked=true
PC14-OSC32_IN\ (PC14).Signal=GPIO_Input
PC15-OSC32_OUT\ (PC15).GPIOParameters=GPIO_PuPd,GPIO_Label
PC15-OSC32_OUT\ (PC15).GPIO_Label=key_add
PC15-OSC32_OUT\ (PC15).GPIO_PuPd=GPIO_PULLUP
PC15-OSC32_OUT\ (PC15).Locked=true
PC15-OSC32_OUT\ (PC15).Signal=GPIO_Input
PC6.GPIOParameters=PinState,GPIO_Label
PC6.GPIO_Label=DISP_A
PC6.Locked=true
PC6.PinState=GPIO_PIN_SET
PC6.Signal=GPIO_Output
PC7.GPIOParameters=PinState,GPIO_Label
PC7.GPIO_Label=DISP_E
PC7.Locked=true
PC7.PinState=GPIO_PIN_SET
PC7.Signal=GPIO_Output
PD0.GPIOParameters=GPIO_Label
PD0.GPIO_Label=DISP_DIG4
PD0.Locked=true
PD0.Signal=GPIO_Output
PD1.GPIOParameters=PinState,GPIO_Label
PD1.GPIO_Label=DISP_L
PD1.Locked=true
PD1.PinState=GPIO_PIN_SET
PD1.Signal=GPIO_Output
PD2.GPIOParameters=PinState,GPIO_Label
PD2.GPIO_Label=DISP_DIG5
PD2.Locked=true
PD2.PinState=GPIO_PIN_RESET
PD2.Signal=GPIO_Output
PD3.GPIOParameters=PinState,GPIO_Label
PD3.GPIO_Label=DISP_G2
PD3.Locked=true
PD3.PinState=GPIO_PIN_SET
PD3.Signal=GPIO_Output
PinOutPanel.RotationAngle=0
ProjectManager.AskForMigrate=true
ProjectManager.BackupPrevious=false
ProjectManager.CompilerLinker=GCC
ProjectManager.CompilerOptimize=6
ProjectManager.ComputerToolchain=false
ProjectManager.CoupleFile=false
ProjectManager.CustomerFirmwarePackage=
ProjectManager.DefaultFWLocation=true
ProjectManager.DeletePrevious=true
ProjectManager.DeviceId=STM32G030C6Tx
ProjectManager.FirmwarePackage=STM32Cube FW_G0 V1.6.2
ProjectManager.FreePins=false
ProjectManager.HalAssertFull=false
ProjectManager.HeapSize=0x200
ProjectManager.KeepUserCode=true
ProjectManager.LastFirmware=true
ProjectManager.LibraryCopy=0
ProjectManager.MainLocation=Core/Src
ProjectManager.NoMain=false
ProjectManager.PreviousToolchain=
ProjectManager.ProjectBuild=false
ProjectManager.ProjectFileName=PulseGenerator.ioc
ProjectManager.ProjectName=PulseGenerator
ProjectManager.ProjectStructure=
ProjectManager.RegisterCallBack=
ProjectManager.StackSize=0x400
ProjectManager.TargetToolchain=MDK-ARM V5.32
ProjectManager.ToolChainLocation=
ProjectManager.UAScriptAfterPath=
ProjectManager.UAScriptBeforePath=
ProjectManager.UnderRoot=false
ProjectManager.functionlistsort=1-SystemClock_Config-RCC-false-HAL-false,2-MX_GPIO_Init-GPIO-false-HAL-true,3-MX_DMA_Init-DMA-false-HAL-true,4-MX_ADC1_Init-ADC1-false-HAL-true,5-MX_TIM1_Init-TIM1-false-HAL-true,6-MX_TIM3_Init-TIM3-false-HAL-true,7-MX_TIM16_Init-TIM16-false-HAL-true,8-MX_TIM14_Init-TIM14-false-HAL-true,9-MX_TIM17_Init-TIM17-false-HAL-true
RCC.ADCFreq_Value=60000000
RCC.AHBFreq_Value=60000000
RCC.APBFreq_Value=60000000
RCC.APBTimFreq_Value=60000000
RCC.CortexFreq_Value=60000000
RCC.EXTERNAL_CLOCK_VALUE=12288000
RCC.FCLKCortexFreq_Value=60000000
RCC.FamilyName=M
RCC.HCLKFreq_Value=60000000
RCC.HSE_VALUE=8000000
RCC.HSI_VALUE=16000000
RCC.I2C1Freq_Value=60000000
RCC.I2S1Freq_Value=60000000
RCC.IPParameters=ADCFreq_Value,AHBFreq_Value,APBFreq_Value,APBTimFreq_Value,CortexFreq_Value,EXTERNAL_CLOCK_VALUE,FCLKCortexFreq_Value,FamilyName,HCLKFreq_Value,HSE_VALUE,HSI_VALUE,I2C1Freq_Value,I2S1Freq_Value,LSCOPinFreq_Value,LSE_VALUE,LSI_VALUE,MCO1PinFreq_Value,PLLN,PLLP,PLLPoutputFreq_Value,PLLR,PLLRCLKFreq_Value,PWRFreq_Value,SYSCLKFreq_VALUE,SYSCLKSource,USART1Freq_Value,VCOInputFreq_Value,VCOOutputFreq_Value
RCC.LSCOPinFreq_Value=32000
RCC.LSE_VALUE=32768
RCC.LSI_VALUE=32000
RCC.MCO1PinFreq_Value=60000000
RCC.PLLN=15
RCC.PLLP=RCC_PLLP_DIV6
RCC.PLLPoutputFreq_Value=40000000
RCC.PLLR=RCC_PLLR_DIV4
RCC.PLLRCLKFreq_Value=60000000
RCC.PWRFreq_Value=60000000
RCC.SYSCLKFreq_VALUE=60000000
RCC.SYSCLKSource=RCC_SYSCLKSOURCE_PLLCLK
RCC.USART1Freq_Value=60000000
RCC.VCOInputFreq_Value=16000000
RCC.VCOOutputFreq_Value=240000000
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

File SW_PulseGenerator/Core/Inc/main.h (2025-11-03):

/* USER CODE BEGIN Header */
/**
  ******************************************************************************
  * @file           : main.h
  * @brief          : Header for main.c file.
  *                   This file contains the common defines of the application.
  ******************************************************************************
  * @attention
  *
  * Copyright (c) 2025 STMicroelectronics.
  * All rights reserved.
  *
  * This software is licensed under terms that can be found in the LICENSE file
  * in the root directory of this software component.
  * If no LICENSE file comes with this software, it is provided AS-IS.
  *
  ******************************************************************************
  */
/* USER CODE END Header */

/* Define to prevent recursive inclusion -------------------------------------*/
#ifndef __MAIN_H
#define __MAIN_H

#ifdef __cplusplus
extern "C" {
#endif

/* Includes ------------------------------------------------------------------*/
#include "stm32g0xx_hal.h"

/* Private includes ----------------------------------------------------------*/
/* USER CODE BEGIN Includes */

/* USER CODE END Includes */

/* Exported types ------------------------------------------------------------*/
/* USER CODE BEGIN ET */

/* USER CODE END ET */

/* Exported constants --------------------------------------------------------*/
/* USER CODE BEGIN EC */

/* USER CODE END EC */

/* Exported macro ------------------------------------------------------------*/
/* USER CODE BEGIN EM */
HAL_StatusTypeDef HAL_TIM_PWM_PWMN_Start(TIM_HandleTypeDef *htim, uint32_t Channel);
HAL_StatusTypeDef HAL_TIM_PWM_PWMN_Stop(TIM_HandleTypeDef *htim, uint32_t Channel);
HAL_StatusTypeDef HAL_TIM_PWM_PWMN_Start_IT(TIM_HandleTypeDef *htim, uint32_t Channel);
HAL_StatusTypeDef HAL_TIM_PWM_PWMN_Stop_IT(TIM_HandleTypeDef *htim, uint32_t Channel);

void led_task(void);
void KeyStaIn(uint8_t num, uint8_t sta);


/* USER CODE END EM */

void HAL_TIM_MspPostInit(TIM_HandleTypeDef *htim);

/* Exported functions prototypes ---------------------------------------------*/
void Error_Handler(void);

/* USER CODE BEGIN EFP */

/* USER CODE END EFP */
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

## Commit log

2025-06-11 Update main.c
    dac范围改为0-3.2V
2025-06-12 update
    增加设置数字位数和清初末尾数字
2025-10-27 更新
    增加了一个电阻，可以极大的减少低压输出的振铃
    [disp.kicad_sch, power.kicad_sch, pulsecal.kicad_pcb, pulsecal.kicad_sch]
2025-10-27 update
    范围改成2mV-999mV
    [pulsecal.kicad_pcb, pulsecal.kicad_sch]
2025-10-28 update v1.2
    改连接器，改贴片器件为直插器件
    [disp.kicad_sch, power.kicad_sch, pulsecal.kicad_pcb, pulsecal.kicad_sch]
2025-10-29 UPDATE
    改连接器和输入电路
    [disp.kicad_sch, pulsecal.kicad_sch]
2025-11-04 update
    增加了多点校准，
2025-11-05 update
    增加了开机显示version，增加了3d打印的文件
    [print3D.3mf, 底部支架.STEP, 电池盒限位.STEP, 电池盒限位small.STEP]
